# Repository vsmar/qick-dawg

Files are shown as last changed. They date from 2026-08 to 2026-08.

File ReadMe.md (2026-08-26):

# QICK-DAWG

## Quantum Instrumentation Control Kit - <br/>Defect Arbitrary Waveform Generator 
<p align="center">
    QD logo
</p>

## Description
The Quantum Instrumentation Control Kit - Defect Arbitrary Waveform Generator (QICK-DAWG) is an extension of [QICK](https://github.com/openquantumhardware/qick) with the purpose of controlling nitrogen-vacancy in diamond and other quantum defects for quantum sensing and other quantum applications.  QICK-DAWG utilizes Xilinx Radio Frequency System-on-Chip (RFSoC) Field Programmable Gate Array (FPGAs) evaluation boards which are significantly less expensive than hardware currently available and have the potential for superior capabilities.

In this package we supply specific mw, laser, and readout pulsing code to characterize  photoluminescence intensity, optically detected magnetic resonance (ODMR), spin readout, Rabi Oscillation, Hahn Echo T<sub>2</sub>, and T<sub>1</sub> relaxation. A Jupyter Notebook Demo is included for performing all of these measurements with an RFSoC4x2 to demonstrate typical measurements. 

## Hardware

- [RFSoC4x2](https://www.xilinx.com/support/university/xup-boards/RFSoC4x2.html),   [ZCU111](https://www.xilinx.com/products/boards-and-kits/zcu111.html) and now supporting the [ZCU216](https://www.amd.com/en/products/adaptive-socs-and-fpgas/evaluation-boards/zcu216.html)
- Control Computer
- Router (required if using LAN connection) [(example)](https://www.amazon.com/TP-Link-Integrated-Lightening-Protection-TL-R605/dp/B08QTXNWZ1/ref=asc_df_B08QTXNWZ1/?tag=hyprod-20&linkCode=df0&hvadid=475692076734&hvpos=&hvnetw=g&hvrand=3761702075041011209&hvpone=&hvptwo=&hvqmt=&hvdev=c&hvdvcmdl=&hvlocint=&hvlocphy=1022494&hvtargid=pla-1149738264234&psc=1) and ethernet cords

## Installation
To install QICKDAWG software follow the README found [here](./installation/Readme.md). Software installation includes:
- necessary hardware for the RFSoC4x2, ZCU111 and ZCU216
- cloning QICK-DAWG
- installing necessary packages for the control computer/FPGA
- connecting to the FPGA

## Usage
QICKDAWG has programs for the characterization of:
- Photoluminescence (PL) Intensity
- Optically Detected Magnetic Resonance (ODMR)
- Readout Window
- Rabi Oscillations 
- Hanhn Echo T<sub>2</sub>
- T<sub>1</sub> Relaxation
- Ramsey Interferometry 

using a ZCU111, RFSoC4x2 and now the ZCU216!

<!-- ### Example use: ###

Optically Detected Magnetic Resonance (ODMR) is one of the QICKDAWG demo pulse sequences. To run ODMR, and any of the other pulse sequences, you must first set the default configuration. The following code, found in the demo Jupyter Notebook, sets the deault configuration.
<p align="center">
    <img src="graphics/config_example.PNG"
        alt="configuration code example"
        width="500x"/>
</p>

The following code copies the default configuration, adjusts a a few configuration settings, and runs ODMR. This code is found in the demo Jupyter Notebook. 

<p align="center">
    <img src="graphics/odmr_example_code.PNG"
        alt="configuration code example"
        width="400x"/>
</p>

The pulse sequencing for ODMR is configured in LockinODMR.py as: 

<p align="center">
    <img src="graphics/odmr_pulse.jpg"
        alt="pulse sequencing for ODMR "
        width="300x"/>
</p>

This is a graph of microwave frequency (MHz) versus ODMR contrast made from data collected using the QICKDAWG ODMR pulse sequencing.

<p align="center">
    <img src="graphics/odmr_example_graph.png"
        alt="pulse sequencing for ODMR "
        width="200x"/>
</p>
 -->

## Support
To raise an issue use the Issues button on the side bar. Email Andy Mounce at amounce@sandia.gov for further support. 

## Authors and acknowledgment
Andy Mounce<sup>[1](#CINT)</sup>, Emmeline Riendeau<sup>[1](#CINT),[2](#Hav),[3](#Chi)</sup> 

<a name="CINT">1</a>: Center for Integrated Nanotechnology (CINT), Sandia National Laboratories<br>
<a name="Hav">2</a>: Haverford College '24 <br>
<a name="Chi">3</a>: UChicago Physics Graduate Program

Thank you to Sho Uemura at Fermi Labs for helping us edit the QICK firmware. 

## License
MIT License 

Copyright 2023 National Technology & Engineering Solutions of Sandia, LLC (NTESS). Under the terms of Contract DE-NA0003525 with NTESS, the U.S. Government retains certain rights in this software.

Permission is hereby granted, free of charge, to any person obtaining a copy
of this software and associated documentation files (the "Software"), to deal
in the Software without restriction, including without limitation the rights
to use, copy, modify, merge, publish, distribute, sublicense, and/or sell
copies of the Software, and to permit persons to whom the Software is
furnished to do so, subject to the following conditions:

The above copyright notice and this permission notice shall be included in all
copies or substantial portions of the Software.

THE SOFTWARE IS PROVIDED "AS IS", WITHOUT WARRANTY OF ANY KIND,
EXPRESS OR IMPLIED, INCLUDING BUT NOT LIMITED TO THE WARRANTIES OF
MERCHANTABILITY, FITNESS FOR A PARTICULAR PURPOSE AND NONINFRINGEMENT.
IN NO EVENT SHALL THE AUTHORS OR COPYRIGHT HOLDERS BE LIABLE FOR ANY CLAIM,
DAMAGES OR OTHER LIABILITY, WHETHER IN AN ACTION OF CONTRACT, TORT OR
OTHERWISE, ARISING FROM, OUT OF OR IN CONNECTION WITH THE SOFTWARE OR THE USE
OR OTHER DEALINGS IN THE SOFTWARE.

## Project status
QICKDAWG project is active and updates will be added as changes are made.

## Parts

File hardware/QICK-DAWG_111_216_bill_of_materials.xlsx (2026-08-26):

Designator | Component | Quanity | Cost Per Unit (USD) | Total (USD) | Source (link) | Material | Required By
RFSoC ZCU216 FPGA | 122-EK-U1-ZCU216-V1-G-ND | 1 | 18762.00 | $18762 | https://www.digikey.com/en/products/detail/amd/EK-U1-ZCU216-V1-G/14292308 | Other | Base
ZCU216 FPGA Enclosure | 111enclosure main.sldprt (CAD files) | 1 | $1089 | $1089 | https://github.com/sandialabs/qick-dawg/tree/main/hardware | Metal | Base
RFSoC ZCU111 FPGA | EK-U1-ZCU111-G | 1 | $16967.85 | $16967.85 | https://www.digikey.com/en/products/detail/amd/EK-U1-ZCU111-G/9655153 | Other | Base
ZCU111 FPGA Enclosure | 216enclosure main.sldprt (CAD files) | 1 | $1390 | $1390 | https://github.com/sandialabs/qick-dawg/tree/main/hardware | Metal | Base
Type A USB cable | AK670/2-1-BLACK | 1 | $2.31 | $2.31 | https://www.digikey.com/en/products/detail/assmann-wsw-components/AK670-2-1-BLACK/2391702 | Other | Base
SMA Panel Mount | ADP-SMAF-SMAF-B-G | 6 | $4.90 | $29.40 | https://www.digikey.com/en/products/detail/te-connectivity-linx/ADP-SMAF-SMAF-B-G/11314389 | Other | Base
12 Pin PMOD Header | G800W590018EU | 1 | $0.21 | $0.21 | https://www.digikey.com/en/products/detail/amphenol-cs-commercial-products/G800W590018EU/13682991 | Other | Base
12 Pin PMOD cable | IDSD-06-D-08.00-T | 1 | $5.96 | $5.96 | https://www.digikey.com/en/products/detail/samtec-inc/IDSD-06-D-08-00-T/9719603 | Other | Base
Screw | 4-40 machine Screw 9900 | 25 | $1.81 | $1.81 | https://www.digikey.com/en/products/detail/keystone-electronics/9900/317321 | Metal | Base
Hex post | 2061-440-S-12 | 20 | $1.11 | $22.20 | https://www.digikey.com/en/products/detail/raf-electronic-hardware/2061-440-S-12/9835526 | Metal | Base
Ethernet cable | N002-002-BK | 1 | $2.12 | $2.12 | https://www.digikey.com/en/products/detail/eaton-tripp-lite/N002-002-BK/4438376 | Other | Base
Managed ethernet router | TP-Link ER605 v2 | 1 | $57 | $57 | https://www.amazon.com/TP-Link-Integrated-Lightening-Protection-TL-R605/dp/B08QTXNWZ1?hvadid=475692076734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 | Other | LAN
SMA Cables (12 in) | BU-4150081012 | 12 | $30.54 | $366.48 | https://www.digikey.com/en/products/detail/mueller-electric-co/BU-4150081012/24637560 | Other | Base

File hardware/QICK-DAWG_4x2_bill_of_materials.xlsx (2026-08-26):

Designator | Component | Quanity | Cost Per Unit (USD) | Total (USD) | Source (link) | Material | Required By
RFSoC4x2 FPGA | RFSoC4x2 | 1 | $2149 | $2149 | https://www.realdigital.org/hardware/rfsoc-4x2 | Other | Base
4x2 FPGA Enclosure w/ lid | 4x2enclosure main.sldprt (CAD files) | 1 | $1390 | $1390 | https://github.com/sandialabs/qick-dawg/tree/main/hardware | Metal | Base
Type A USB cable | AK670/2-1-BLACK | 1 | $2.31 | $2.31 | https://www.digikey.com/en/products/detail/assmann-wsw-components/AK670-2-1-BLACK/2391702 | Other | Base
SMA surface mount Panel Mount | ADP-SMAF-SMAF-B-G | 6 | $4.53 | $27.18 | https://www.digikey.com/en/products/detail/te-connectivity-linx/ADP-SMAF-SMAF-B-G/11314389 | Other | Base
12 pin PMOD Header | G800W590018EU | 1 | $0.18 | $0.18 | https://www.digikey.com/en/products/detail/amphenol-cs-commercial-products/G800W590018EU/13682991 | Other | Base
12 Pin PMOD cable | IDSD-06-D-08.00-T | 1 | $5.13 | $5.13 | https://www.digikey.com/en/products/detail/samtec-inc/IDSD-06-D-08-00-T/9719603 | Other | Base
Screw | 4-40 machine Screw | 25 | $1.50 | $1.50 | https://www.digikey.com/en/products/detail/keystone-electronics/9900/317321 | Metal | Base
Hex post | 2061-440-S-12 | 20 | $0.92 | $18.40 | https://www.digikey.com/en/products/detail/raf-electronic-hardware/2061-440-S-12/9835526 | Metal | Base
Ethernet cables | N002-002-BK | 1 | $2.12 | $2.12 | https://www.digikey.com/en/products/detail/eaton-tripp-lite/N002-002-BK/4438376 | Other | Base
Managed ethernet router | TP-Link ER605 v2 | 1 | $57 | $57 | https://www.amazon.com/TP-Link-Integrated-Lightening-Protection-TL-R605/dp/B08QTXNWZ1?hvadid=475692076734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 | Other | LAN
SMA Cables (12 in ) | BU-4150081012 | 6 | $30.54 | $183.24 | https://www.digikey.com/en/products/detail/mueller-electric-co/BU-4150081012/24637560 | Other | Base

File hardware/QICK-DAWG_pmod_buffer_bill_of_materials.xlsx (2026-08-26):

Name | Component | Quantity | Cost Per Unit (USD) | Total (USD) | Supplier Source
SMA Female Panel Mount | PCB.114SMAFSTJ.A | 8 | $4.50 | $36.00 | https://www.digikey.com/en/products/detail/taoglas-limited/PCB-114SMAFSTJ-A/15998672
Low-Side Gate Driver | LM5114BMF/NOPB | 8 | $1.86 | $14.88 | https://www.digikey.com/en/products/detail/texas-instruments/LM5114BMF-NOPB/3137454
10 µF 16V Ceramic Capacitor | CL21A106KOQNNNE | 8 | $0.08 | $0.64 | https://www.digikey.com/en/products/detail/samsung-electro-mechanics/CL21A106KOQNNNE/3886754
0 Ohms Jumper Chip Resistor | ERJ-6GEY0R00V | 16 | $0.10 | $1.60 | https://www.digikey.com/en/products/detail/panasonic-electronic-components/ERJ-6GEY0R00V/78163
4.7 kOhms Chip Resistor | CRCW08054K70FKEAC | 1 | $0.10 | $0.10 | https://www.digikey.com/en/products/detail/vishay-dale/CRCW08054K70FKEAC/7928553
Green 520nm LED Indication | 150060GS75000 | 1 | $0.15 | $0.15 | https://www.digikey.com/en/products/detail/w%C3%BCrth-elektronik/150060GS75000/4489898
Connector Header Through Hole | G800W590018EU | 2 |  |  | https://www.digikey.com/en/products/detail/amphenol-cs-commercial-products/G800W590018EU/13682991
USB-A 2.0 Receptacle Connector | USB-A-S-RA-TSMT | 1 | $0.63 | $0.63 | https://www.digikey.com/en/products/detail/adam-tech/USB-A-S-RA-TSMT/9832331
USB-A 2.0 cable | AK670/2-1-BLACK | 1 | $2.31 | $2.31 | https://www.digikey.com/en/products/detail/assmann-wsw-components/AK670-2-1-BLACK/2391702
Ribbon Cable | IDSD-06-D-08.00-T | 1 | $5.96 | $5.96 | https://www.digikey.com/en/products/detail/samtec-inc/IDSD-06-D-08-00-T/9719603
(Optional)Connector Header Through Hole | G800W590018EU | 1 | $0.15 | $0.15 | https://www.digikey.com/en/products/detail/amphenol-cs-commercial-products/G800W590018EU/13682991

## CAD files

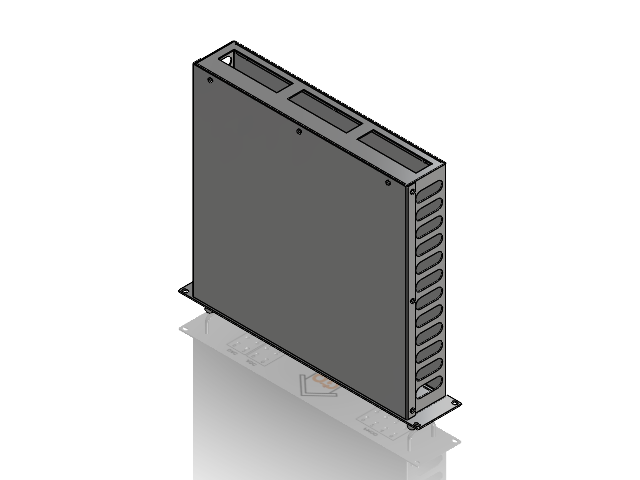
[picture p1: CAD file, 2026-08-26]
hardware/DAWG_House_4x2/4x2_enclosure_main.SLDASM
Chassis_1.stp
6-32_3_8in_natural_phillips_panhead_screw_1.stp
6-32_3_8in_natural_phillips_panhead_screw-0_1.stp
SP-832-1_1.stp
SP-832-1-1_1.stp
SP-832-1-2_1.stp
6-32_3_8in_natural_phillips_panhead_screw-3_1.stp
6-32_3_8in_natural_phillips_panhead_screw-4_1.stp
SP-832-1-5_1.stp
SP-832-1-6_1.stp
SP-832-1-7_1.stp
FH4-832-6_1.stp
FH4-832-6-8_1.stp
FH4-832-6-9_1.stp
Cover_1.stp
8-32_3_8in_natural_phillips_panhead_screw_1.stp
8-32_3_8in_natural_phillips_panhead_screw-10_1.stp
8-32_3_8in_natural_phillips_panhead_screw-11_1.stp
8-32_3_8in_natural_phillips_panhead_screw-12_1.stp
8-32_3_8in_natural_phillips_panhead_screw-13_1.stp
8-32_3_8in_natural_phillips_panhead_screw-14_1.stp
8-32_3_8in_natural_phillips_panhead_screw-15_1.stp
8-32_3_8in_natural_phillips_panhead_screw-16_1.stp
8-32_3_8in_natural_phillips_panhead_screw-17_1.stp
Rear_1.stp
SP-832-1-18_1.stp
SP-832-1-19_1.stp
SP-832-1-20_1.stp
Front_1.stp
Small_Rackmount_Handle_Sweep_1.stp
Small_Rackmount_Handle_Sweep-21_1.stp
FH4-832-6-22_1.stp

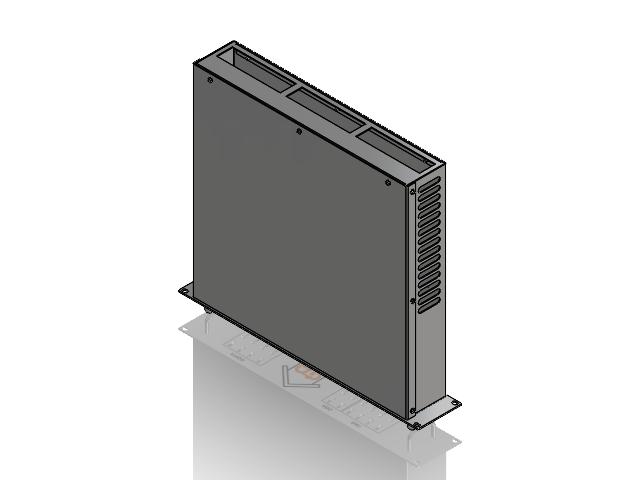
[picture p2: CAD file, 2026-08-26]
hardware/DAWG_House_ZCU111/ZCU111_enclosure_main.SLDASM
Chassis_1.stp
6-32_3_8in_natural_phillips_panhead_screw_1.stp
6-32_3_8in_natural_phillips_panhead_screw-0_1.stp
SP-832-1_1.stp
SP-832-1-1_1.stp
SP-832-1-2_1.stp
6-32_3_8in_natural_phillips_panhead_screw-3_1.stp
6-32_3_8in_natural_phillips_panhead_screw-4_1.stp
SP-832-1-5_1.stp
SP-832-1-6_1.stp
SP-832-1-7_1.stp
FH4-832-6_1.stp
FH4-832-6-8_1.stp
FH4-832-6-9_1.stp
Cover_1.stp
8-32_3_8in_natural_phillips_panhead_screw_1.stp
8-32_3_8in_natural_phillips_panhead_screw-10_1.stp
8-32_3_8in_natural_phillips_panhead_screw-11_1.stp
8-32_3_8in_natural_phillips_panhead_screw-12_1.stp
8-32_3_8in_natural_phillips_panhead_screw-13_1.stp
8-32_3_8in_natural_phillips_panhead_screw-14_1.stp
8-32_3_8in_natural_phillips_panhead_screw-15_1.stp
8-32_3_8in_natural_phillips_panhead_screw-16_1.stp
8-32_3_8in_natural_phillips_panhead_screw-17_1.stp
Rear_1.stp
SP-832-1-18_1.stp
SP-832-1-19_1.stp
SP-832-1-20_1.stp
Front_1.stp
Small_Rackmount_Handle_Sweep_1.stp
Small_Rackmount_Handle_Sweep-21_1.stp
FH4-832-6-22_1.stp

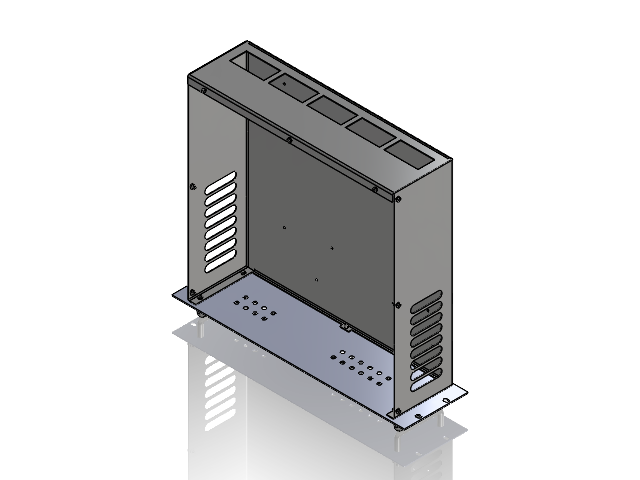
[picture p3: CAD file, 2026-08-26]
hardware/DAWG_House_ZCU216/ZCU216_enclosure_main.SLDASM
Chassis.stp
8-32_3_8in_natural_phillips_panhead_screw.stp
8-32_3_8in_natural_phillips_panhead_screw-0.stp
S-832-1ZI.stp
S-832-1ZI-1.stp
S-832-1ZI-2.stp
8-32_3_8in_natural_phillips_panhead_screw-3.stp
8-32_3_8in_natural_phillips_panhead_screw-4.stp
S-832-1ZI-5.stp
S-832-1ZI-6.stp
S-832-1ZI-7.stp
FH-832-6ZI.stp
FH-832-6ZI-8.stp
FH-832-6ZI-9.stp
8-32_3_8in_natural_phillips_panhead_screw-10.stp
8-32_3_8in_natural_phillips_panhead_screw-11.stp
8-32_3_8in_natural_phillips_panhead_screw-12.stp
8-32_3_8in_natural_phillips_panhead_screw-13.stp
8-32_3_8in_natural_phillips_panhead_screw-14.stp
8-32_3_8in_natural_phillips_panhead_screw-15.stp
8-32_3_8in_natural_phillips_panhead_screw-16.stp
8-32_3_8in_natural_phillips_panhead_screw-17.stp
8-32_3_8in_natural_phillips_panhead_screw-18.stp
Rear.stp
S-832-1ZI-19.stp
S-832-1ZI-20.stp
S-832-1ZI-21.stp
Front.stp
Medium_Rackmount_Handle_Sweep.stp
Medium_Rackmount_Handle_Sweep-22.stp
FH-832-6ZI-23.stp

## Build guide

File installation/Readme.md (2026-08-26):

# RFSoC4x2, ZCU111 and ZCU216 setup (WAN, direct internet connection)
This Readme supports setting up your selected RFSoC FPGA, where it's connected directly to the internet--Wide Area Network (WAN). 

The RFSoC4x2, as shown in the image below, is a board built and sold by [Real Digital](https://www.realdigital.org/) using AMD’s ZYNQ Ultrascale+ Gen 3 RFSoC ZU48DR chip.  While the ZU48DR has eight digital-to-analog converters (DACs) and analog-to-digital converters (ADCs), the RFSOC4x2 only uses four DACs (5 GSa/s) and two ADCs (9.85 GSa/s). Nonetheless, this number of inputs and outputs is nearly perfect for NV and quantum defect control. 

<!-- However, as the RFSOC4x2 is sold, the ADCs have a high frequency 1GHz high-pass balun inline which is typically too high frequency for our measurements and thus must be modified. -->

<p align="center">
    RFSoC4x2 with inputs and outputs labelled

</p>

The ZCU216 and ZCU11 as shown in the images belows, are evaluation boards built by AMD using Zynq UltraScale+ RFSoC chips. The ZCU216 uses the on the ZU49DR chip, featuring 16 ADCs (2.5 GSa/s) and 16 DACs (9.85 GSa/s). The ZCU11 uses the ZU28DR chip, offering 8 ADCs (4.096 GSa/s) and 8 DACs (6.554 GSa/s).

<!-- However, as the RFSOC4x2 is sold, the ADCs have a high frequency 1GHz high-pass balun inline which is typically too high frequency for our measurements and thus must be modified. -->

<p align="center">
    ZCU111 Evaluation Board

</p>

<p align="center">
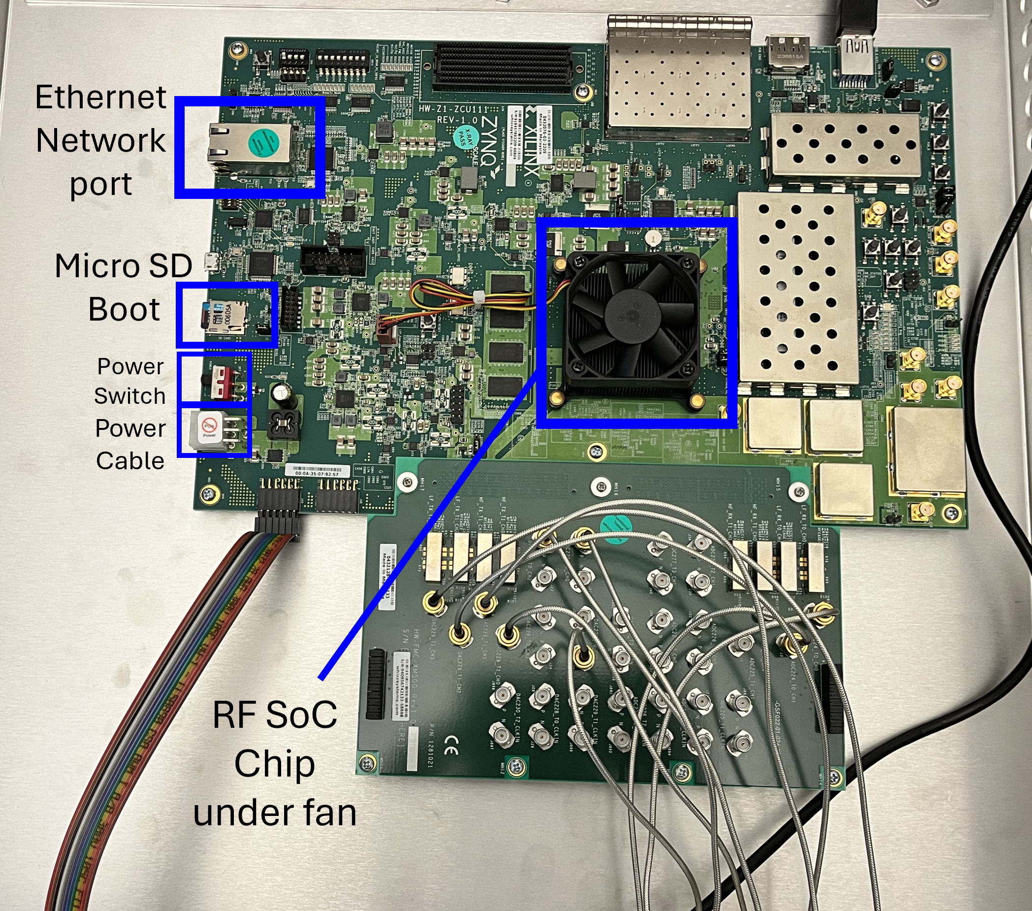
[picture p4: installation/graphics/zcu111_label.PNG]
ZCU111 Evaluation Board
    

</p>
In this document we outline the setup for using QICK-DAWG with a RFSoC4x2, ZCU111 and ZCU216. Specifically, we show how to:

1. Install QICK-DAWG and other software to your RFSoC FPGA <br>
    a. Flash your microSD card<br>
    b. Clone QICK-DAWG on your RFSoC FPGA <br>
    c. Install necessary packages on your RFSoC FPGA <br>
    d. Run the Pyro server to remotely connect to QICK and the RFSoC FPGA<br>

2. Setup lab control computer<br>
    a. Download/clone QICK-DAWG <br>
    b. Install necessary packages<br>

3. Setup RFSoC FPGA Hardware<br>
    <!-- a. Photon counting mode<br> -->
    <!-- b. Low frequency analog modification<br> -->
    <!-- c. Connect PMOD digital outputs<br> -->
    a. Buffer board setup
    b. Assemble and power on your RF SoC FPGA <br>
    c. (Optional) Full enclosure assembly

## ***Prerequisites***
<!-- #### For initial setup: -->
<!-- - See xxxx build files for more details. -->
- [RFSoC4x2](https://www.xilinx.com/support/university/xup-boards/RFSoC4x2.html) (with 12 volt 50 watt power supply)
- [ZCU216](https://www.amd.com/en/products/adaptive-socs-and-fpgas/evaluation-boards/zcu216.html)
- [ZCU111](https://www.amd.com/en/products/adaptive-socs-and-fpgas/evaluation-boards/zcu111.html)
- Ethernet cord
- Micro SD card reader
<!-- (DC Mode) -->
<!-- - Low frequency differential amplifier [Texas Instruments LMH5401EVM](https://www.digikey.com/en/products/detail/texas-instruments/LMH5401EVM/5031896?s=N4IgTCBcDaIDIFkASBWALABgIwFEBqCIAugL5A) -->
<!-- - 3 x DC output voltage supply (+3.2, +0.7, -1.8V for biasing the differential amplifier) -->
- SMA cables

### Software 
- [Win32DiskImager](https://sourceforge.net/projects/win32diskimager/) for Windows or Disk Manager on MacOS
- Dependent packages (follow `Installing Necessary Packages` section--included in the setup batch file)
    - [QICK](https://github.com/openquantumhardware/qick)

# 1. Install QICK-DAWG and other software to your RFSoC FPGA 
<!-- This file no longer exists.. -->
<!-- (Getting started directions adapted from [QICK ZCU111 quick-start-guide](https://github.com/openquantumhardware/qick/blob/main/quick_start/README_ZCU111.md)) -->

## 1a. Flash your Micro SD Card ##
- First, you will need to flash the micro SD card with the appropiate PYNQ image file for your selected RFSoC FPGA. Download the RFSoC PYNQ image and unzip the file if it is a .zip file. Lastest and older versions are avaiable.
   - **RFSoC4x2 PYNQ** v3.1.1 image found [here](https://www.pynq.io/boards.html). 
   - **ZCU111** v3.1.1 image found [here](https://www.pynq.io/boards.html)
   - **ZCU216** found [here](https://github.com/sarafs1926/ZCU216-PYNQ)

(Windows)
- With your micro SD card plugged in to your computer, open Win32DiskImager. Select the PYNQ file as your image file and select your micro SD card as the device. Double check you are not flashing the image file to the wrong drive (**not your computer hard drive**)! To execute, click `Write`. 

<p align="center">
    Flashing your micro SD card using Win 32 Disk Imager
</p>

Once the image is written to the microSD card, put the microSD card into the RFSoC FPGA, connect to the internet via ethernet, and turn the board on. 
On the RFSoC4x2, the LED screen on top of the board will have your ip address which you will need for further steps. 

<!-- To setup your own static IP for the ZCU216 and ZC111:
- When connected to the board on the linux command line type: `*vim etc/networks/interfaces.d/eth0`
- For ethernet port `*eth0`, change `*iface eth0 inet dynamic` to `*iface eth0 inet dynamic`
- Save and exit
- Ensure on the Host machine the gateway IP on your selected ehternet port to the FPGA is static (i.e 192.168.0.1) and your ipv4 net is set static as well (i.e 192.168.0.xxx) -->

## 1b. Clone QICK-DAWG on your FPGA ##

SSH directly into the board using it's IP via windows cmd.exe with the command,

`ssh xilinx@{ip address}`

You will then be prompted for the password, which is also `xilinx` and asked to store the ssh footprint, for which you should respond `yes`. 
Now you'll have remote, terminal control of the board.  From here type

```
cd ./jupyter_notebooks
git clone https://github.com/sandialabs/qick-dawg

```
This will download the qick-dawg repository to the default directory of the jupyter notebook server run by the RFSoC FPGA.
If you cannot clone the qick-dawg repo from the board, clone it locally on your Host machine and copy it over the FPGA via scp, 

`scp qick-dawg/ xilinx@{ip address}:/jupyter_notebooks/`

## 1c. Install necessary Packages on your RFSoC FPGA ##
With the required files copied to your RFSoC FPGA, we will now install the required packages by running an .ipynb though the FPGA's Jupyter Notebook server. To connect to the jupyter notebook server:

In a browser window type your FPGA's IP address and use password `xilinx` as shown in the graphic below

<p align="center">
    Initial view of Jupyter Hub
</p>
 
From the home page, navigate to the installation folder, open install_packages.ipynb and run all of the cells to install the packages. This does three things:

1. installs pyro4 for remote control of the board
2. downloads and installs qick
3. moves some files around

## 1d. Run the Pyro server to remotely connect to QICK and the RFSoC FPGA ##

With all of the packages installed, you can now run your Pyro server to connect to an instance of QICK. This is accomplished by running two jupyter notebooks. 

- First we run `run_server/name_server.ipynb` which starts a Pyro server. In this notebook, you need to change the IP address to the IP address of your board. 
<p align="center">
    Name Server
</p>

- Second, we run the `run_server/qick_daemon.ipynb` notebook, which uploads firmware to the FPGA and creates a python socket to communicate with the board. This notebook has a string which contains the path to our alternative firmware and has a `ns_host` variable which needs to be assigned to the IP address of your RFSoC4x2 board. 
<p align="center">
    Name Server
</p>

With these two notebooks running you can now start communicating with your FPGA from a python kernel on your Host computer. From here, we recommend running through `qickdawg/jupyter_notebooks/` which contains significant documentation on how to run our basic NV characterization notebooks. 

Note that the qick_daemon notebook specifically points to a firmware made for qick-dawg.

# 2. Setup lab control computer

## 2a. Download/clone a local copy QICK-DAWG
You need a local copy of QICK-DAWG on your lab control computer. There are two options for obtaining a local copy of QICK-DAWG

1.  use a git manager to clone QICK-DAWG, found at `https://github.com/sandialabs/qick-dawg` (on Windows, VSCode is nice for this)
2.  download QICK-DAWG as a .zip file from the [GitHub repository](https://github.com/sandialabs/qick-dawg) and unzip it. 

## 2b. Install Necessary Packages
To run your FPGA from your lab computer you need to install QICK-DAWG. To install QICK-DAWG, on your lab computer:

- In the command prompt navigate to `*\qick-dawg`
- Enter `pip install -e ./`

This will install QICK-DAWG and it's dependent packages. 

## Running demo notebooks

With the remote pyro4 server running on the FPGA and qick-dawg installed on your local computer you should now be able to connect to the demo notebooks in the /qick-dawg/jupyter_notebooks folder. 

# 3. Setup Your FPGA Hardware 
<!-- Is this section needed now? -->
## 3a. Photon counting mode

The ADC inputs on the RFSoC4x2 have baluns inline which act like long pass filters.  When we first made QICK-DAWG we had to bypass these for photodiode readout.  However, for single photon countings from a single photon detector module, the TTLs generate by each photon arrival can pass through the balun with sufficent signal to be counted.  Thus a single photon detector can be directly plugged into an ADC for counting mode as demo'd in coutning_demo_RFSoC4x2.ipynb.

<!-- To setup for this demo, plug your microwave amplifier into DAC_B and your single photon detector into ADC_D. Additionally, connect your laser gate into PMOD 0 (section 3c). -->

<!-- ## 3b. Low frequency analog readout

The ADCs on the RFSoC must be modified because ~1MHz signal measured by the photodiodes cannot be directly connected to the ADCs on the board.  The ADCs on the RFSoC4x2 have baluns and capacitors that act as high pass filters. When using photodiodes for photoluminesence detection, the signal is low frequency, therefore unmodified ADCs do not let the signal from the photodiodes pass. Given this, the balun must be removed and the capacitors bypassed to readout the signal from the photodiodes with the ADCs. Furthermore, as the ADCs take in a differential voltage signal, we have to add a differential amplifier which takes the signal from the photodetector in and outputs a biased signal to the ADCs for digitization (see section 1.b below). 

The input electronics for one ADC channel on the RFSoC4x2 is shown in the figure below.  

<figure>
    <p align="center">
        <img src="graphics/balun_circuit.PNG"
            alt="Balun Surgery"
            width="1000px"/>
    </p>
    <!-- <figcaption align="center">Circuit diagram for the RFSoC4x2 ADC D. (Left - Circled) Balun to be removed (Right - Circled) Solder input leads to the far side of the capacitors </figcaption>
</figure> -->

<!-- The combination of the balun (MABA-801111) and the two 100nF capacitors (C302 and C303) result in a high pass filter. In order to collect the signal, we need to remove the balun and bypass the capacitors. Our clumsy method is to pull off the balun (under an RF shield) and solder input wires on the down current side of the capacitors. 

<p align="center">
    <img src="graphics/balun_bypass.png"
        alt="Balun Surgery"
        width="1000px"/>
</p> -->

<!-- ## Connect the low frequency differential amplifier -->

<!-- To properly condition our signal for digitization, we use a Texas Instruments  [Texas Instruments LMH5401 EVM](https://www.digikey.com/en/products/detail/texas-instruments/LMH5401EVM/5031896?s=N4IgTCBcDaIDIFkASBWALABgIwFEBqCIAugL5A) evaluation board. This board takes in one or two signals and outputs two voltages above (V<sub>p</sub>) and below (V<sub>m</sub>) a common voltage (V<sub>cm</sub>). For full scale, the RFSoC4x2 requires an offset voltage of V<sub>cm</sub> = 0.7V (note that this is also true for the ZCU216 evaluation board, but the ZCU111 evaluation board requires V<sub>cm</sub> = 1.2 V). Additionally, the differential amplifier requires two voltages for power, which are optimally set to (V<sub>cm</sub> + 2.5) = 3.2V and (V<sub>cm</sub> - 2.5 )= -1.8.  A labeled diagram of the LMH5401EVN is shown in the figure below.  

<p align="center">
    <img src="graphics/differential_amp.PNG"
        alt="Balun Surgery"
        width="450px"/>
</p>

To connect the low frequency differential amplifier to the RFSoC4x2,

- solder a 3.3 V input wire to the red V+ post on the low frequency differential amplifier;
- solder a -1.8 V input wire to the yellow V- post on the low frequency differential amplifier;
- screw a 0.7 V SMA wire to the Vcm (V common) SMA head on the top of the low frequency differential amplifier;
- cut a semi-flexible SMA cable in half and strip the insulation off of both ends to expose the center conductor ;
- screw the SMA heads of the cut SMA cable to Vp and Vm SMA heads on the low frequency differential amplifier--screwing on the SMA cables now will limit the torsion on our delicate soldering in the next steps;
- take the SMA cables attached to the low frequency differential amplifier and solder them to the RFSoC4x2.
    - Vp should be soldered to the far side of the top capacitor
    - Vm should be soldered to the far side of the bottom capacitor

The image below is an image of the diff amp wired to the capacitors and the balun removed for a working RFSoC4x2 with DC inputs.

<p align="center">
    <img src="graphics/balun_bypass_2.png"
        alt="balun_bypass_2"
        width="1000px"/>     
</p>

RFSoC4x2 Schematic <sup>[1](#RFSoc4x2_Schematic)</sup>

Note if you are worried about removing the balun from your RFSoC4x2, marketplaces such as Digikey sell replacement baluns which can be used to restore the functionality of modified ADCs in the future. 
 -->
<!-- To connect, we cut the female head off a PMOD cable and soldered on a female BNC head instead. PMOD A 0-7 are enabled for QICK-DAWG (in the demo we use PMOD 0). The image below provides a schematic of the PMOD on the RFSoC4x2. -->

<p align="center">
    PMOD diagram
</p>

## 3b. Assemble and power on your FPGA board

With the hardware setup and PMOD Buffer board connected, the FPGA can be assembled to be connected to your computer. This connection is made with a WAN connection and a router. To do so:
- slide your micro SD card into its slot on the FOGA board and check that the BOOT switch is on SD mode; 
- connect an Ethernet cable from the board to the router;
- and connect the FPGA to its power supply and turn it on.

You should hear the fan above the RFSoC chip begin to whir and you should see green LED lights blinking all over the board. On the 4x2, after about 30 seconds the boot light should turn green and the LED screen will display the board's IP address. Your setup should resemble the schematic below. 

### Wiring and Powering the Buffer Board
There are three wiring tasks for the enclosure: main power, the PMOD buffer board, and the final network connections. The PMOD TTL outputs are connected by first plugging in a 12-pin PMOD Header connector, which mates with one end of the 12 pin PMOD cable to the FPGA’s PL PMOD. Place the buffer board in the designated PMOD slot on the front panel of the enclosure labeled ”PMOD”. Ensure that the corresponding pin numbers on the buffer board align with those on the front label of the panel. The buffer board will be powered using a type A USB connector and the available USB 2.0 port on the FPGA. To allow power through the USB 2.0 port on the ZCU111 and ZCU216, the USB port must be enabled through jumper settings on the board to supply power to the buffer board. For the ZCU111, a jumper should be place on J17 GND and SHLD. For the ZCU216 at J19 HOST and J20 GND and SHLD. 

#### Final connections and setup
Finally, the Ethernet port of the RFSoC can be connected either directly to the host machine or to one channel of a router, with a second cable connecting another channel of the router to the Ethernet port of the FPGA. With all components assembled, the RFSoC firmware should be flashed to a microSD card as indicated in the installation section of https://github.com/sandialabs/qickdawg.

<!-- ???? -->
<!-- <p align="center">
    <img src="graphics/RFSoC_Diagram_WAN.png"
        alt="Diagram of the RFSoC4x2 Board"
        width="800px"/>
</p> --> -->

## 3c. (Optional) Full enclosure setup

In our lab, we have assembled all the necessary components into a custom rack box ([Bud Industries CH-14404 Enclosure](https://www.digikey.com/en/products/detail/bud-industries/CH-14404/428959)) with screw holes and 3D printed cages for fastening components. Hardware setup instructions for the enclosure can be found on our [QICK-DAWG Read the Docs](https://qick-dawg.readthedocs.io/en/latest/index.html) site. The following CAD files for the enclosure are found in `qickdawg/hardware/DAWG_House_{your FPGA}`:

- enclosure_Main.SLDPRT, CAD for custom enclosure drill holes to secure FPGA and front panel holes for SMA and buffer pass through.
- xxxx_front_graphics, graphics and labels for the front panel of the dawg house.

<!-- - Low_Freq_Diff_Amp_Base.SLDRT, CAD for 3D printable differential amplifier support for mounting the differential amplifier near the RFSoC 4x2 board
- Low-Freq_Diff_Amp_Top.SLDPRT, CAD for 3D printable differential amplifier top
- Router_Holder.SLDPRT, CAD for 3D printable router cage for holding the router in the enclosure -->

<!-- add another picture to replace this below. Older picture shows diff amp and DC mode on  -->
<!-- <p align="center">
    <img src="graphics/Full_enclosure.jpg"
        alt="Full Enclosure "
        width="800px"/>
</p> -->

<!-- While this is listed as optional, for DC mode it is really required to sabilize the differential ampifier relative to the RFSoC4x2.  -->

# References
<a name="RFSoc4x2_Schematic">1</a>: [RFSoC4x2 Schematic](https://www.realdigital.org/downloads/3ae3a2552d7da46e9041196c654cd63d.pdf)

<a name="Qick">2</a>: [QICK Repository](https://github.com/openquantumhardware/qick)

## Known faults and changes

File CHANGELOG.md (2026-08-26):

## [1.2.2](https://github.com/sandialabs/qick-dawg/compare/v1.3.1...v1.2.2) (2026-06-02)

### Reverts

* Revert "Reapply "fix: fixed bugs realted to laseron/off and softavg still being required (#64) [skip ci]"" ([4b1a1bf](https://github.com/sandialabs/qick-dawg/commit/4b1a1bf85e5544f468d2987da0700c5e52e38114)), closes [#64](https://github.com/sandialabs/qick-dawg/issues/64)
* Revert "Reapply "fix: fixed bugs realted to laseron/off and softavg still being required (#64) [skip ci]"" ([1365275](https://github.com/sandialabs/qick-dawg/commit/1365275bf9e05e8dfe84009b76fe365c5e0fa8a3)), closes [#64](https://github.com/sandialabs/qick-dawg/issues/64)
* Revert "fix: fixed bugs realted to laseron/off and softavg still being required (#64) [skip ci]" ([07b49a6](https://github.com/sandialabs/qick-dawg/commit/07b49a69ccd49818d188575b29848fac119842bf)), closes [#64](https://github.com/sandialabs/qick-dawg/issues/64)
* reverting to 2.302 compatibility, few bug fixes ([5bd6708](https://github.com/sandialabs/qick-dawg/commit/5bd6708c27633a9459542ea636632face15deb7a))

## [1.3.1](https://github.com/sandialabs/qick-dawg/compare/v1.3.0...v1.3.1) (2026-06-01)

### Bug Fixes

* fixed bugs realted to laseron/off and softavg still being required ([5f9f394](https://github.com/sandialabs/qick-dawg/commit/5f9f39483025c5ea85c897ff62670ccd3dd036c9))
* fixed bugs realted to laseron/off and softavg still being required ([#64](https://github.com/sandialabs/qick-dawg/issues/64)) [skip ci] ([7380e0d](https://github.com/sandialabs/qick-dawg/commit/7380e0d2eadd2e178f1d1f01d2afa26a20c733be))

# [1.3.0](https://github.com/sandialabs/qick-dawg/compare/v1.2.1...v1.3.0) (2026-05-30)

### Features

* Latest DAWG house build files for 4x2, ZCU111 and ZCU216. ([bfe67b4](https://github.com/sandialabs/qick-dawg/commit/bfe67b4e9a750a4b2e12f3220f2754a101a9faa0))

## [1.2.1](https://github.com/sandialabs/qick-dawg/compare/v1.2.0...v1.2.1) (2025-01-29)

### Bug Fixes

* fixed installation to remove qd install and paths ([033c254](https://github.com/sandialabs/qick-dawg/commit/033c254772d211be45b8f4bffe012e33bde48643))
* fixed installation to remove qd install and paths ([#53](https://github.com/sandialabs/qick-dawg/issues/53)) [skip ci] ([f405d28](https://github.com/sandialabs/qick-dawg/commit/f405d28dfd9857fbbaeb1ac119cf4a48b840d733))

# [1.2.0](https://github.com/sandialabs/qick-dawg/compare/v1.1.0...v1.2.0) (2025-01-17)

### Features

* **photon_counting:** confirmed photon counting works for all pulse sequences ([8b2b19b](https://github.com/sandialabs/qick-dawg/commit/8b2b19be11afb0ecf28463a3fcdd160128649500))

# [1.1.0](https://github.com/sandialabs/qick-dawg/compare/v1.0.2...v1.1.0) (2025-01-15)

### Bug Fixes

* changed analysis to consistently have contrast as just the difference ([99f3689](https://github.com/sandialabs/qick-dawg/commit/99f3689193fd52b401bf3cee09f1952e2b7336fa))
* **client:** fixed start client for remote use ([da3c227](https://github.com/sandialabs/qick-dawg/commit/da3c2276c963aa9c76bbd9d7c68178ad4ae74255))
* fixing integration of photon counting with newest version ([2b2b561](https://github.com/sandialabs/qick-dawg/commit/2b2b561c756487008b7e4c56eef0b44696a88c99))
* **graphics:** fixed the graphics path error ([a0bd964](https://github.com/sandialabs/qick-dawg/commit/a0bd96457cf18ea79692b7e475bb2adfe1770714))
* **install:** added itemattribute to the requirements list ([ea95c23](https://github.com/sandialabs/qick-dawg/commit/ea95c23445867eadc1b8c0477992633d63e7c3c2))
* **installation:** simplified package installation, only supporting online installs ([7989c24](https://github.com/sandialabs/qick-dawg/commit/7989c249ffe6b410dbbd6b7fa39e393d4a25b44a))
* **itemattribute:** used pypi itemattribute with correct item assignment ([9279638](https://github.com/sandialabs/qick-dawg/commit/9279638c9bc8ed6e4b199c472c506f9e55cb58db))
* **pulsing:** small pulsing changes with integrated ddr4 and testing ([1243e80](https://github.com/sandialabs/qick-dawg/commit/1243e80d6f1d9627afd71e34390caa14125c4dba))
* **t1:** swapped pulsing order for consistent analysis ([6cadb08](https://github.com/sandialabs/qick-dawg/commit/6cadb082b20df814686d5ce70dc8401c4769297c))
* updated qick version requirement to include remote fix ([bfb8c05](https://github.com/sandialabs/qick-dawg/commit/bfb8c05bb2530416193ddb9f0598999db0bcc4aa))

### Features

* added NVAverageprogram.setup_readout to setup analog or digital readout ([f63008a](https://github.com/sandialabs/qick-dawg/commit/f63008a0d3586949d7d911eefccbc9332204a8c1))
* added simple read out window to calibrate photon ttl levels ([1518307](https://github.com/sandialabs/qick-dawg/commit/1518307846dac81afcc4606da0b73067339839df))
* added simple read out window to calibrate photon ttl levels ([a73505e](https://github.com/sandialabs/qick-dawg/commit/a73505e80e438c17fc321d48ae5deafeb4cdf8a2))
* **client:** Added local mode to start client ([e9121ee](https://github.com/sandialabs/qick-dawg/commit/e9121ee119d2ba81568bd14a6e318cfa29ad14a1))
* **cpmgxy8:** Added cpmgxy8, delay sweep demonstrated ([b361e42](https://github.com/sandialabs/qick-dawg/commit/b361e42a9190cae5599c9dfe2a913e920fce82f1))
* Lockin-ODMR now has counting mode and analyze digital or analog ([d1f25c1](https://github.com/sandialabs/qick-dawg/commit/d1f25c1bb5800fba44cf702ecb164f1e4864daf2))
* PLIntensity now works with edge counting, analysis can be rate or total ([95c3447](https://github.com/sandialabs/qick-dawg/commit/95c34478b1f7bb7e3624fb21d4c7f24681c056ff))
* updated laser on/off to read out single TTLs from edge counting mode ([9e979d9](https://github.com/sandialabs/qick-dawg/commit/9e979d997c2af625dfaef0ec865570041c5ba267))

## [1.0.2](https://github.com/sandialabs/qick-dawg/compare/v1.0.1...v1.0.2) (2024-12-18)

### Bug Fixes

* **pulse_readout:** pulse readout end was slightly off ([68eb37b](https://github.com/sandialabs/qick-dawg/commit/68eb37bbc09b0becce2c9c51757ab560665bcc9a))
* **rabi:** fixed rabi sequence, dropped 'length' syntax ([bdb7407](https://github.com/sandialabs/qick-dawg/commit/bdb7407917c73408db28b36c23d1107017f970ad))
* **readoutwindow:** modified readoutwindow so that it doesn't use sycnall ([b1bdc86](https://github.com/sandialabs/qick-dawg/commit/b1bdc86db1e95ef05f6c863b5a5d07347a42a6c7))

## [1.0.1](https://github.com/sandialabs/qick-dawg/compare/v0.0.6...v1.0.1) (2024-10-12)

### Bug Fixes

* **meta:** fixed import so it's no longer broken ([98db853](https://github.com/sandialabs/qick-dawg/commit/98db853614c61325841e4fc83b7cc3555bbff4d5))
* **meta:** fixed import so it's no longer broken ([#47](https://github.com/sandialabs/qick-dawg/issues/47)) [skip ci] ([4c4ef57](https://github.com/sandialabs/qick-dawg/commit/4c4ef57527fa38b323606968fb581aa23d2860ff))

## [0.0.6](https://github.com/sandialabs/qick-dawg/compare/v0.2.0...v0.0.6) (2024-10-09)

### Bug Fixes

* **init:** updated init message ([efe2b00](https://github.com/sandialabs/qick-dawg/commit/efe2b0069b64a1edfb3cd989c3ddffb5b6a658fa))
* **meta:** changed convetional commits and corrected errors for autotesting: ([677d035](https://github.com/sandialabs/qick-dawg/commit/677d0355731042d4142a0ed91cc9e24716fe7648))
* **pyproject:** fixed missing quote ([74d003c](https://github.com/sandialabs/qick-dawg/commit/74d003cbac645499a1f91a53a4684f74488ca458))
* started to fix NVAverager Program ([a01aa6e](https://github.com/sandialabs/qick-dawg/commit/a01aa6e1859e35dda76d260663103359143b7715))
* **upgrade qick:** upgraded to qick 0.2.289. BREAKING CHANGE ([ebd083b](https://github.com/sandialabs/qick-dawg/commit/ebd083bbd998da5d6e7d683302d700ed3c51e693))

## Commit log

2025-11-07 Improved the commenting for subnano_res CPMG
    [Waveform-Amplitude-10000.csv, Waveform-Amplitude-12000.csv, Waveform-Amplitude-14000.csv, Waveform-Amplitude-15000.csv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]
2025-11-19 Updated CPMG subnano, to use waveform address manipulation instead of binary search tree. Added phase and sequencing improvements.
    [Waveform-Amplitude-10000.csv, Waveform-Amplitude-12000.csv, Waveform-Amplitude-14000.csv, Waveform-Amplitude-15000.csv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]
2026-02-25 Added PODMR, and added functionality to the counting demo notebook, this is starting to get too complicated for an introductory user. Will need to split to a new subdirectory for future updates.
    [all_odmrs.csv, odmr_000.csv, odmr_001.csv, odmr_002.csv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]
2026-03-05 Overhauled RF testing files, and naming structure, and testing notebook, added a physical delay test.
    [Waveform-Amplitude-10000.csv, Waveform-Amplitude-12000.csv, Waveform-Amplitude-14000.csv, Waveform-Amplitude-15000.csv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]
2026-03-12 Bug fix with the delays and phase for PulsePol, and modifications to testing notebook
    [PulsePolDev_Scope_Waveform.csv]
2026-03-18 added fine res rabi and counting duration files based on Tommy's ARQICK code
    [podmr_hyperfine_polarized_2026-03-16_19-31-58.csv, podmr_hyperfine_polarized_2026-03-16_19-58-55.csv]
2026-03-18 Restructure the workflow to have config.yaml, and experiment specific python files for headless execution
    [PulsePolDev_Scope_Waveform.csv]
2026-03-20 Successful integration of podmr, rabi and cpmg, into pipleine for rapid workflow. Unified the data storing structure and experiment files to rely on shared functions. Implemented and tested working C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
    [bootstrap_experiment_1845MHz.csv, bootstrap_experiment_1846MHz.csv, bootstrap_experiment_1847MHz.csv, cpmg_n16_500_10100.csv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]
2026-03-23 Refactored plotting logic. Added fine timing units to nvconfiguration.py and refactored sequences and experiment files to utilize.
    [counting_duration.csv, run_summary.csv]
2026-03-26 Added relaxation and decoherence 200ps experiments
    [counting_duration.csv, cpmg_n16_500_10100.csv, cpmg_n8_500_10100.csv, run_summary.csv]
2026-03-31 Fixed critical error in CPMG regarding the interpulse spacing between pi pulses
    [cpmg_normalized_combined.csv, minion_Do_combined_runs_signal_normalized.csv, minion_Do_cpmg_0-pop_tau-corrected.csv]
2026-04-15 Commit before cleaning up repo
    [cpmg_reopt_run_20260331_182347_sweep_correct_tau.csv, cpmg_reopt_run_20260331_182347_sweep_correct_tau_rolling_norm.csv]
2026-04-22 Improved commenting for fine res files, still pre-rebase
    [counting_duration.csv, cpmg_normalized_combined.csv, cpmg_reopt_run_20260331_182347_sweep_correct_tau.csv, cpmg_reopt_run_20260331_182347_sweep_correct_tau_rol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]
2026-04-23 notebook progress save
    [counting_duration.csv]
2026-04-27 corrected Fine Time Demo Notebook and cleaned file tree
    [bootstrap_experiment_1845MHz.csv, bootstrap_experiment_1846MHz.csv, bootstrap_experiment_1847MHz.csv, counting_duration.csv]
